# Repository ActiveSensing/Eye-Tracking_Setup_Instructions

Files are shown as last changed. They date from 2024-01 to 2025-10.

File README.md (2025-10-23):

## Required Parts

<b>Thorlabs</b>:
- 1 Dovetail Rail Carrier <a href="https://www.thorlabs.de/thorproduct.cfm?partnumber=RC1">RC1</a>
- 1 Dovetail Optical Rail <a href="https://www.thorlabs.de/thorproduct.cfm?partnumber=RLA075/M">RLA075/M</a>
- 1 Adjustable Flip Platform <a href="https://www.thorlabs.de/thorproduct.cfm?partnumber=FP90/M">FP90/M</a>
- 1 Optical Post TR../M (of the appropriate length. e.g. <a href="https://www.thorlabs.de/thorproduct.cfm?partnumber=TR20/M">TR20/M</a>)
- 1 Post Holder PH../M (of the appropriate length. e.g. <a href="https://www.thorlabs.de/thorproduct.cfm?partnumber=PH20/M">PH20/M</a>)
- (optional) 1 Swivel Base Adapter <a href="https://www.thorlabs.de/thorproduct.cfm?partnumber=UPHA">UPHA</a>
- (optional) 1 Ø12.5 mm Bandpass Filter (Of the approriate filtering range e.g. <a href="https://www.thorlabs.de/thorproduct.cfm?partnumber=FBH05850-10">FBH05850-10 - Hard-Coated</a> for a DPP light of 850nm.

<b>Others suppliers</b>:
- Teledyne's Chameleon3 Camera, model: <a href="https://www.teledynevisionsolutions.com/en-150/products/chameleon3-usb3/?model=CM3-U3-13Y3M-CS&vertical=machine%20vision&segment=iis">CM3-U3-13Y3M-CS</a>
- InfiniStix Lens, model <a href="https://www.edmundoptics.de/p/infinistix-3x-44mm-wd-video-lens/3413/">3X 44mm WD</a>
- Macromanipulator LD40-LM (cheap, Constructor unknown but available on many website)

<b>Homemade Parts</b>:
- One 3D print of all stl files <a href="https://github.com/ActiveSensing/Eye-Tracking_Setup_Instructions/tree/main/Eye%20Camera%20Building%20Instructions/3D%20Printed%20and%20Manufactured%20Parts">here</a>, preferably using an ABS-R black filament

<b>Screws</b>:
- M6 of 10 mm
- M4 of 8mm and 10mm
- M3 of 10mm and 20mm
  
## Assemble Parts

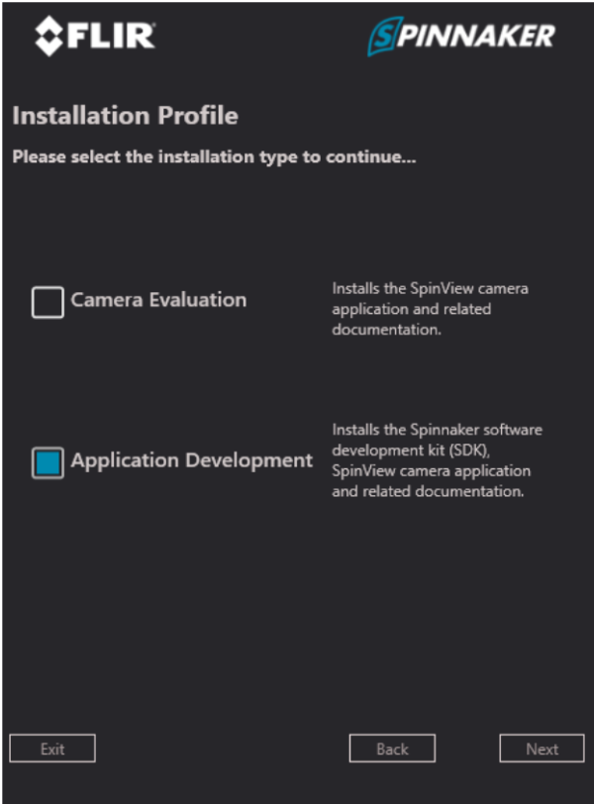
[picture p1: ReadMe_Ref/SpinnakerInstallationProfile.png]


1. Use 4 <b>M3 screws (10mm)</b> to screw the <b>camera</b> onto the flat side of the the <b>CasedRailMicromanipulatorAdaptor</b> 3D-print.

2. Use 1 <b>M6 screw (10mm)</b> to screw the <b>Dovetail Rail Carrier RC1</b> onto the <b>CasedRailMicromanipulatorAdaptor.</b>
    - $\color{red}{\textrm{Make sure that the RC1's thumb screw will face the user.}}$
    - $\color{red}{\textrm{Make sure that the camera cable will point in the most convinient direction within the setup.}}$

3. Use 1 <b>M4 screws (8mm)</b> to screw the <b>Dovetail Rail RLA075/M</b> onto the <b>CasedRailMicromanipulatorAdaptor</b>.
    - $\color{red}{\textrm{Make sure that the base of the Rail lies on the base of the CasedRailMicromanipulatorAdaptor, so the Rail Carrier can attach on top.}}$

4. Use 4 <b>M3 screws (10mm)</b> to screw the <b>CasedRailMicromanipulatorAdaptor</b> onto the top platform of the <b>macromaniplator LD40-LM</b>.
    - $\color{red}{\textrm{Orient the CasedRailMicromanipulatorAdaptor to make sure that the rail will point in the opposite direction than the fly.}}$
    - $\color{red}{\textrm{Orient the macromanipulator to make sure that all knobs will be easily accessible by the user.}}$
    - $\color{red}{\textrm{Depending on which platform of the macromanipulator is the top one, the caps of the screws will be either top or down.}}$

5. Use 4 <b>M4 screws (10mm)</b> to screw the <b>Adjustable Flip Platform FP90/M</b> onto the flatter side of the <b>MicromanipulatorPlatformAdaptor</b>.

6. Use 4 <b>M3 screws (10mm)</b> to screw the <b>MicromanipulatorPlatformAdaptor</b> onto the base platform of the <b>macromaniplator LD40-LM</b>.
    - $\color{red}{\textrm{Make sure that the locking screw of the Adjustable Flip Platform will face the user}}$
    - $\color{red}{\textrm{Make sure that that locking screw will be opposite direction of the fly (so the structure can tilt away from the fly)}}$

7. Use 2 <b>M4 screws (10mm)</b> to screw the <b>postFixer</b> onto the <b>Adjustable Flip Platform FP90/M</b>.

8. Use 1 <b>M3 screws (20mm)</b> to fix the <b>Optical Post</b> onto the <b>postFixer</b>.

9. Fix the <b>Post Holder</b> onto the Setup (More stable if using the optional <b>Swivel Base Adapter</b>).
    - $\color{red}{\textrm{The thumb screw of the Post Holder should face the user}}$

10. Fix the <b>Optical Post</b> into the <b>Post Holder</b>.

11. Fix the <b>Dovetail Rail Carrrier RC1</b> onto the <b>Dovetail Rail RLA075/M</b>.

12. Attach the <b>InfiniStix Lens</b> onto the <b>camera</b>
13. Insert the optional <b>Bandpass filter</b> into the <b>InfiniStix Lens</b> and secure it with the InfiniStix_FilterHolder.stl

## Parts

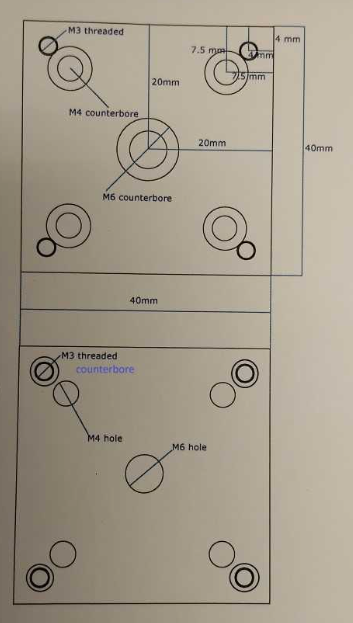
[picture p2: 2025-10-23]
Eye Camera Building Instructions/3D Printed and Manufactured Parts/MicromanipulatorPlatformAdaptor_Blueprint.png

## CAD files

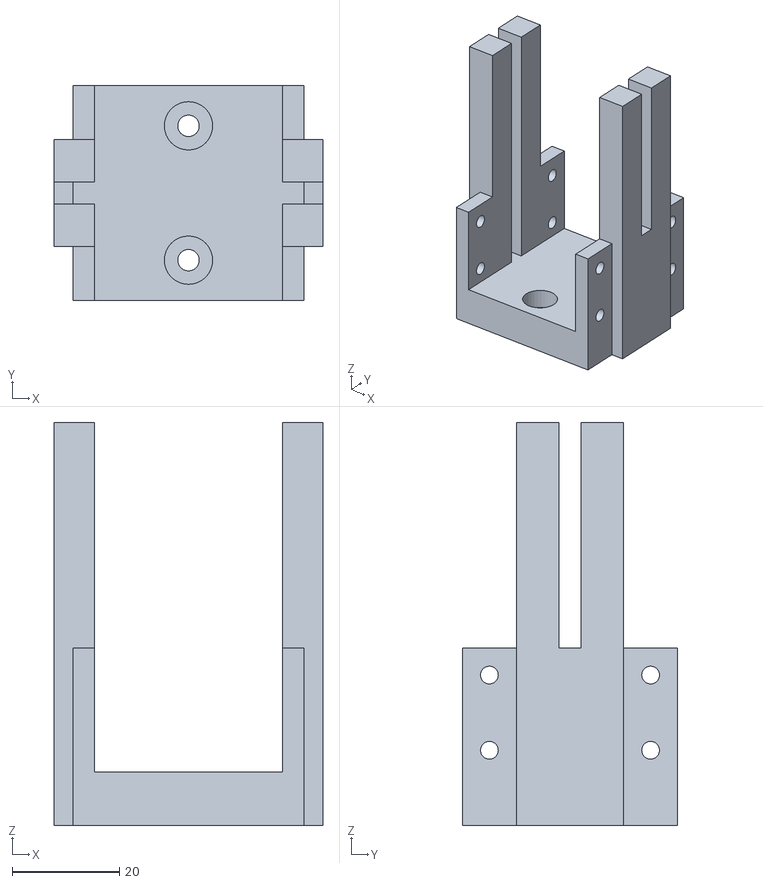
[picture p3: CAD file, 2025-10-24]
Ball Walking Camera Instructions/3D Printed and Manufactured Parts/HorizontalCameraHolder_AndBallHolderStabilizator.stl
50.0 x 40.0 x 75.0

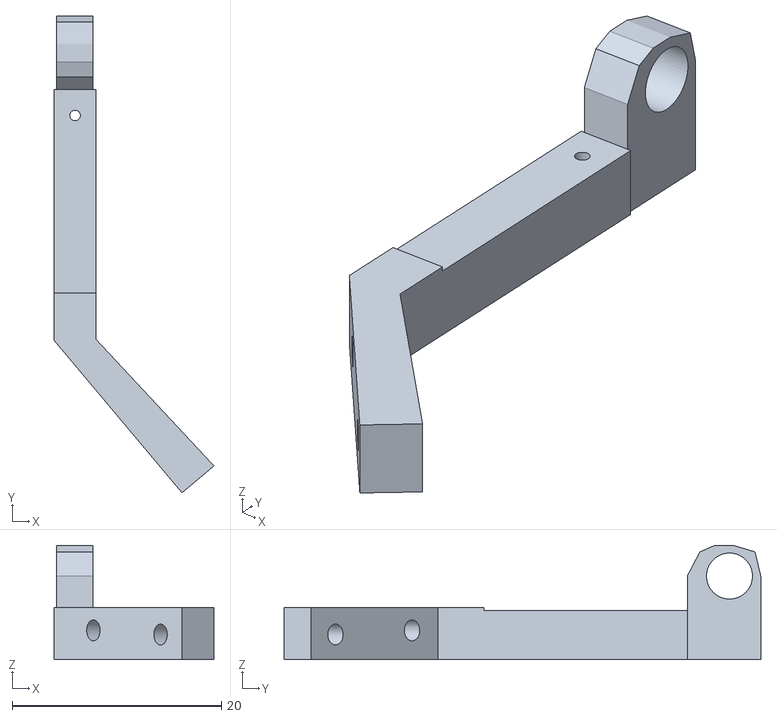
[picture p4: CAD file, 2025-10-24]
Ball Walking Camera Instructions/3D Printed and Manufactured Parts/Second Mirror for Flight/SecondMirrorRotor.stl
15.3 x 45.6 x 10.9

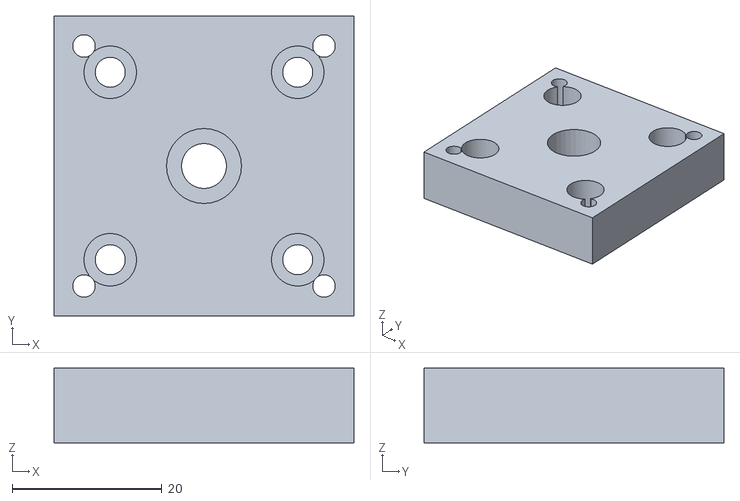
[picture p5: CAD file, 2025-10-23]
Eye Camera Building Instructions/3D Printed and Manufactured Parts/MicromanipulatorPlatformAdaptor.stl
40.0 x 40.0 x 10.0

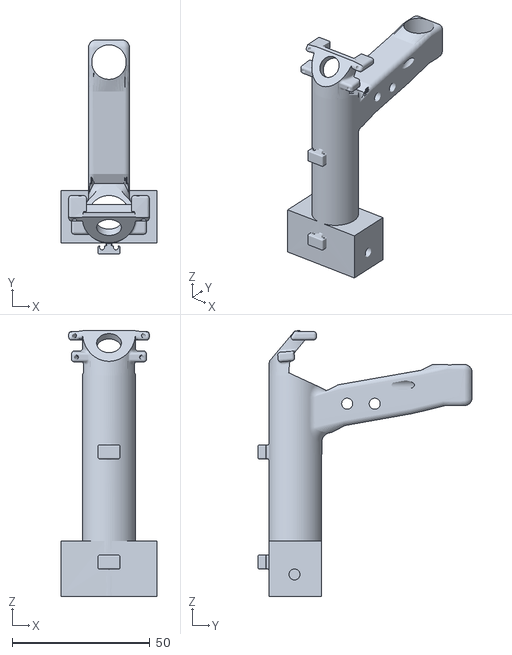
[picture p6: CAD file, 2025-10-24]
Ball Walking Camera Instructions/3D Printed and Manufactured Parts/BallHolder_100Deg.stl
35.0 x 77.9 x 96.6

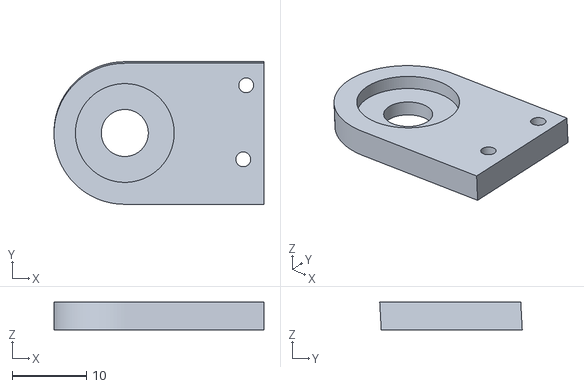
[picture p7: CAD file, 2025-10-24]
Ball Walking Camera Instructions/3D Printed and Manufactured Parts/Second Mirror for Flight/SecondMirrorHolder.stl
28.4 x 19.3 x 3.75

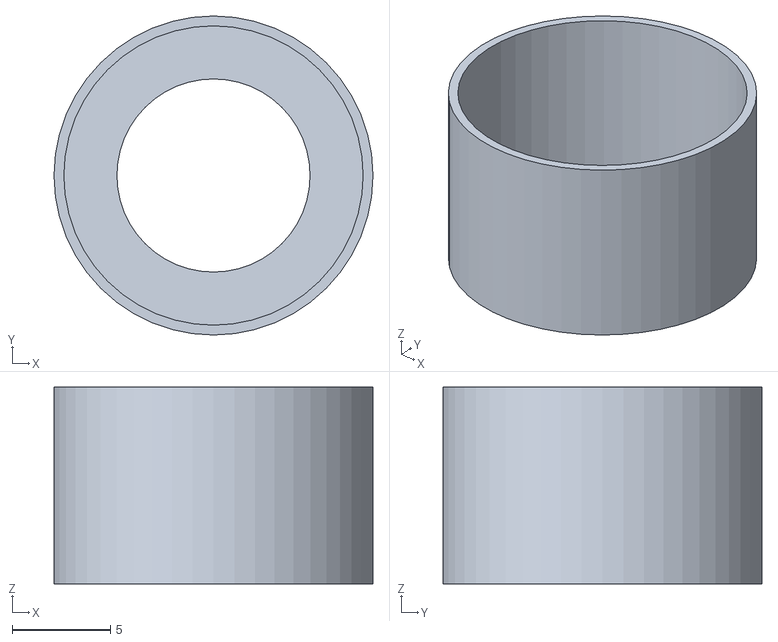
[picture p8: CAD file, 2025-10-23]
Eye Camera Building Instructions/3D Printed and Manufactured Parts/InfiniStix_FilterHolder.stl
16.2 x 16.2 x 10.0

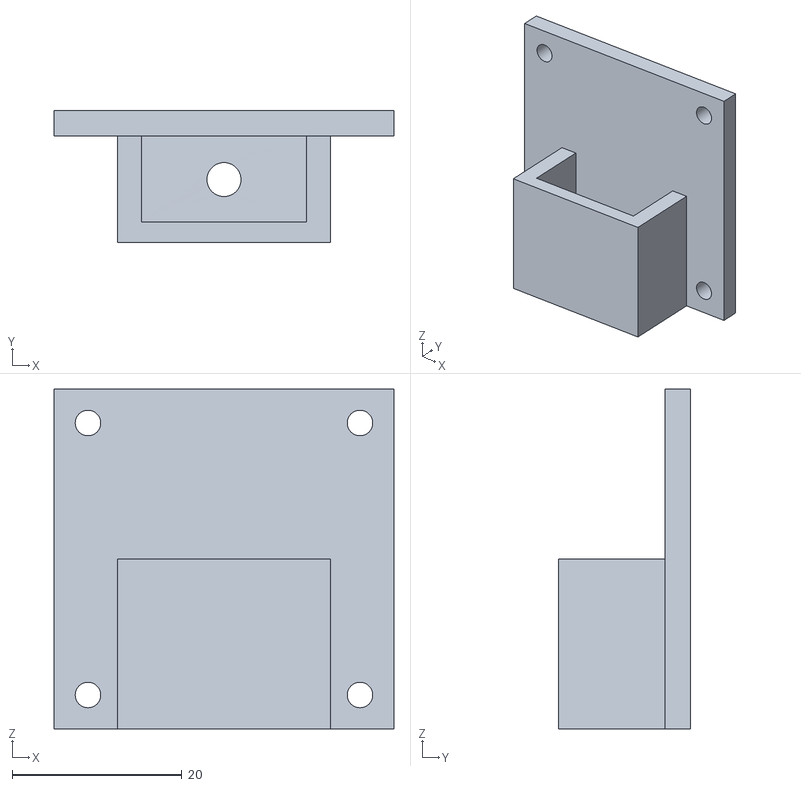
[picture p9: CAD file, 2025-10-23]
Eye Camera Building Instructions/3D Printed and Manufactured Parts/CasedRailMicromanipulatorAdaptor.stl
40.0 x 15.5 x 40.0

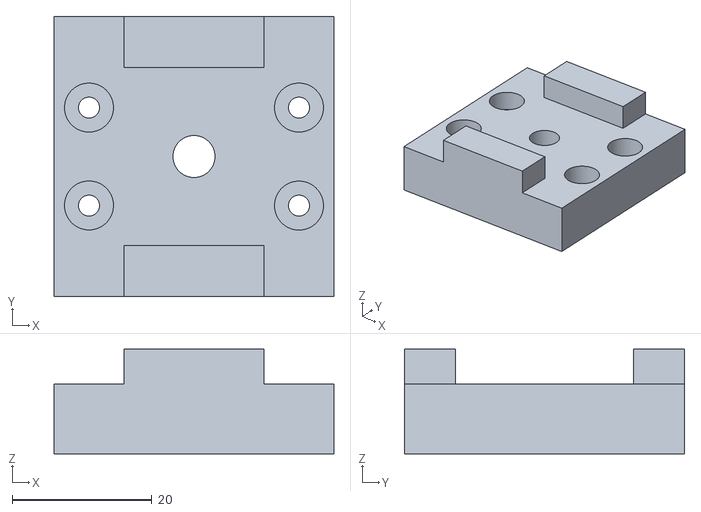
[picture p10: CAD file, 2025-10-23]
Eye Camera Building Instructions/3D Printed and Manufactured Parts/VerticalCameraHolder_RC1.stl
40.0 x 40.0 x 15.0

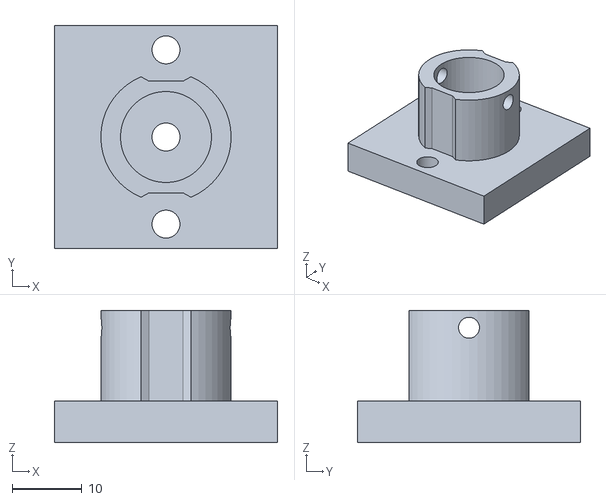
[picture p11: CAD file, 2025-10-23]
Eye Camera Building Instructions/3D Printed and Manufactured Parts/postFixer.stl
32.0 x 32.0 x 19.0

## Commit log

2025-10-23 Revise README with parts and assembly instructions
    Updated the README to include required parts, assembly instructions, and installation steps for software and hardware components.
2025-10-23 Finalize readme for instruction to build eye camera
